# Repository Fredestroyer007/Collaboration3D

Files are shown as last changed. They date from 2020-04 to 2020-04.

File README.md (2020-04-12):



<br />
<br />

Dans ce guide vous allez retrouver toutes les informations requises pour fabriquer vos propres visières par impression 3D pour aider dans la lutte contre COVID-19.

Notre modèle *Jaguar* est une version modifiée du merveilleux modèle conçu par le [Fablab de l'Université Libre de Bruxelles](https://fablab-ulb.gitlab.io/projects/coronavirus/protective-face-shields/). Vous pouvez retrouver leur modèle original [ici](https://gitlab.com/fablab-ulb/projects/coronavirus/protective-face-shields/-/tree/master/PFC-Headband-Light-3DPrint).

Le modèle *Jaguar* peut sembler assez léger et peu résistant, mais je vous assures qu'avec une bonne impression, il est très difficile de casser la visière.

Le coût brut de production estimé est moins de 1$ soit 0,20$ pour le filament, 0,70$ pour la feuille d'acétate et des élastiques. En plus, la durée d'impression par visière est d'environ 20 minutes.

Si vous rencontrer un problème lors de l'impression vous pouvez aller directement à notre [FAQ](#faq). **TODO**

Si vous imprimez le modèle, envoyer nous des photos sur [Facebook](https://www.facebook.com/Collaboration3D/). Nous voulons voir vos résultats!!!

Vous pouvez aussi visiter notre [site web](https://collaboration3d.ca/) pour plus d'information!

Un gros merci à nos commanditaires : le Collège de Bois-de-Boulogne, la fondation de l'Hôpital Sacré-Coeur de Montréal, la firme Laporte et Bureau en gros!

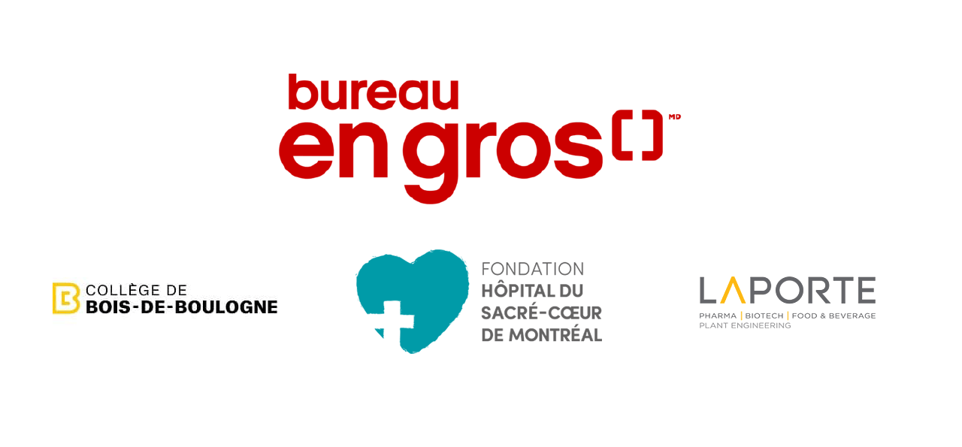
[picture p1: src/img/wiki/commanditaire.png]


Si vous désirez nous commandités, visiter notre [site web](https://collaboration3d.ca/) pour plus d'information!

For the version in English scroll to the end... **TODO**

## Table des matières

* [Pour débuter vous allez avoir besoin de...](#pour-débuter-vous-allez-avoir-besoin-de)
* [Impression 3D](#impression-3d)
  * [Préparation du modèle](#préparation-du-modèle)
    * [Option 1 - Sélectionner un modèle existant](#option-1---sélectionner-un-modèle-existant)
    * [Option 2 - Configurer un modèle selon vos propres besoins](#option-2---configurer-un-modèle-selon-vos-propres-besoins)
      * [Configuration OpenSCAD](#configuration-openscad)
      * [Paramètres](#paramètres)
      * [Exportation](#exportation)
  * [Impression](#impression)
    * [Paramètres obligatoires](#paramètres-obligatoires)
    * [Paramètres optionnels](#paramètres-optionnels)
* [Préparation pour acétate](#préparation-pour-acétate)
* [Préparation pour élastique](#préparation-pour-élastique)
* [Assemblage final](#assemblage-final)
* [Processus de désinfection](#processus-de-désinfection)
* [Avertissement](#avertissement)
* [FAQ](#faq)
* [Auteurs](#auteurs)
* [Licence](#licence)
* [Reconnaissance](#reconnaissance)

## Pour débuter vous allez avoir besoin de...

- Une imprimante 3D 

Tant que la zone d'impression mesure un minimum de 125x125mm vous allez être en mesure d'imprimer les visières. Une surface chauffante est recommendée, mais elle n'est pas essentielle. Utiliser la même méthode d'adhésion que vous utilisez normalement pour du PLA.

- Du filament de type PLA

Peu coûteux, facilement accessible et possible d'imprimer à grande vitesse, le PLA est un matériel idéal pour ce genre d'utilisation. Il faut environ 8g de filament par visière, donc avec une bobine standard de 1kg, vous devriez être en mesure de produire environ 125 visières. Si la production de volume ne vous intéresse pas, vous pouvez aussi utiliser des matériaux comme le PETG, l'ABS, le nylon qui possèdent divers avantages sur le PLA, mais leur vitesse d'impression est plus lente.

- Des feuilles d'acétate de format A4

Vous pourrez en trouver dans les magasins d'articles de bureau.

- Des élastiques

Il faut deux élastiques standard ou vous pouvez concocter votre propre solution pour faire tenir la visière sur la tête.

- Un ordinateur avec [OpenSCAD](https://www.openscad.org/) installé (optionnel) et le logiciel requis pour votre imprimante

Pas besoin d'un ordinateur très puissant, un ordinateur portable fonctionne parfaitement.

- Une perforatrice 3 trous de format nord-américain 4.25" (format de cartable standard au Canada et aux États-Unis)

Plus la capacité est grande, plus votre travail sera facile, vous pourrez faire les trous dans plus d'une feuille d'acétate à la fois.

## Impression 3D
## Préparation du modèle

Sur [la page principale Github](https://github.com/Fredestroyer007/Collaboration3D), cliquer sur « Clone or download » :

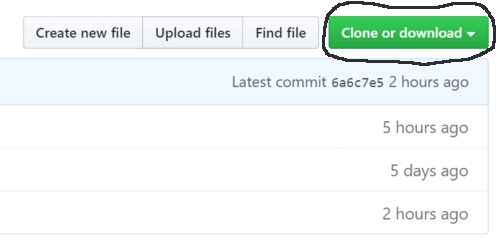
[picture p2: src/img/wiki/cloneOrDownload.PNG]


Ensuite, cliquer sur « Download ZIP » et sélectionner l'endroit que vous désirez télécharger les fichiers sur votre ordinateur :

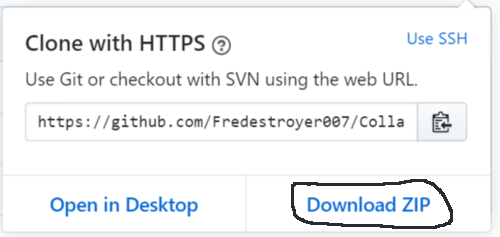
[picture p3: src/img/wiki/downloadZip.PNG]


Ouvrez le dossier compressé et vous avez deux options maintenant.

[La première option](#option-1---sélectionner-un-modèle-existant) est pour un utilisateur moins avancé et [la seconde option](#option-2---configurer-un-modèle-selon-vos-propres-besoins) est pour un utilisateur avancé qui désir optimiser sa production au maximum.

### Option 1 - Sélectionner un modèle existant
Pour débuter, si un modèle existe déjà pour votre configuration d'imprimante, vous devez sélectionner ce modèle. Aller dans le dossier « Modèle », puis « Jaguar ». Ensuite, vous devez sélectionner le dossier correspondant à la hauteur de couche que vous désirez imprimer. À l'intérieur du dossier choisit, vous devez sélectionner le nombre de visière empiler (indiquer par le multiplicateur). Nous vous recommandons de commencer par un nombre plus faible et de lentement augmenter. Vous pouvez ensuite passer à l'étape [Impression](#impression).

### Option 2 - Configurer un modèle selon vos propres besoins!
Si un modèle n'existe pas encore, vous pouvez créer le votre vous-même! La configuration est assez simple!
#### Configuration OpenSCAD
[OpenSCAD](https://www.openscad.org/) est un logiciel gratuit de modélisation CAD paramétrique. Au lieu de modéliser graphiquement un modèle, il est programmer. Cette particularité vous permet d'adapter très facilement le modèle à vos paramètres d'impression.

Après avoir installé [OpenSCAD](https://www.openscad.org/) sur votre ordinateur vous retrouvez le fichier « modification.scad » dans le dossier « CAD » dans le dossier que vous avez télécharger à l'étape précèdente. Cliquer dessus pour lancer le programme :



Une fois dans le programme :

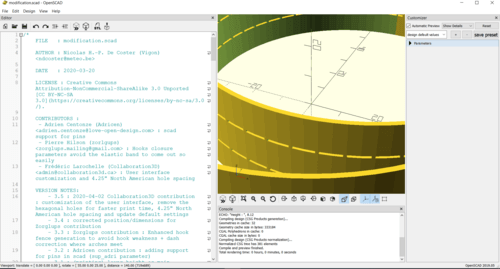
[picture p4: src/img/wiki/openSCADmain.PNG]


Vous pouvez fermer le premier panneau pour créer plus d'espace. Vous n'allez pas avoir besoin de ce panneau. Il s'agit du code source de la pièce :



Sur le panneau de droite « Customizer », cliquer sur « Parameters » pour afficher les paramètres à modifier :

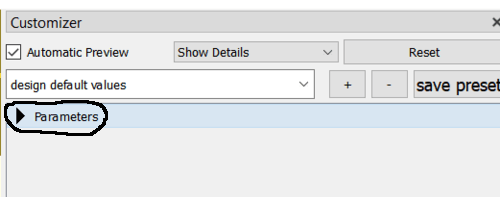
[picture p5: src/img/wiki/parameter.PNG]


Maitenant que l'interface est prêt, à la gauche, vous retrouvez une visualisation de votre modèle et, à la droite, le panneau des paramètres à modifier. Votre interface devrait ressembler à ceci :

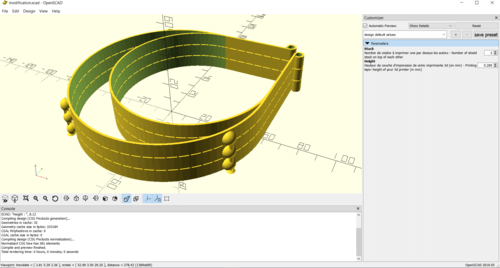
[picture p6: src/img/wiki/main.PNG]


#### Paramètres

Vous avez deux paramètres à modifier. Le premier « Stack » est le nombre de visière empiler que vous désirez imprimer par impression. Nous vous suggérons de commencer par des plus petites valeurs et de lentement augmenter le nombre de visière que vous imprimez à la fois à mesure que vous découvrez les limites de votre imprimante 3D. Le second paramètre est « Height ». Vous devez simplement entrez la valeur de la hauteur d'impression de chaque couche de votre imprimante. Ce paramètre est mieux connu sous le nom anglais « layer height ». Dans les contraintes de votre imprimante, plus ce paramètre est grand, plus l'impression sera rapide. Avec ceci en tête, nous vous recommandons de viser une hauteur de couche de 0.3mm et plus si possible pour votre imprimante. Pour observer l'effet de vos paramètres sur la visualisation, cliquer sur un autre champs de paramètre.

Par exemple, pour une Creality Ender-3, comme paramètre pour débuter, nous vous recommandons d'imprimer trois visières à la fois avec une hauteur de couche de 0.28mm :

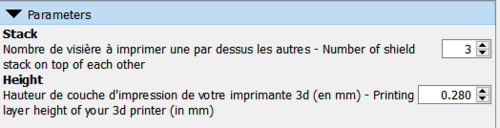
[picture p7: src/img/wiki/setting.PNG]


#### Exportation

Avant d'exporter votre modèle pour impression, vous devez faire le rendu du modèle en cliquant sur F6. Soyez patient. Un modèle volumineux avec plusieurs visières de hauteur peut prendre quelques minutes à faire le rendu. Quand le rendu est finit, vous devriez entendre un son et voir apparaître un message comme celui-ci dans le bas de votre écran :

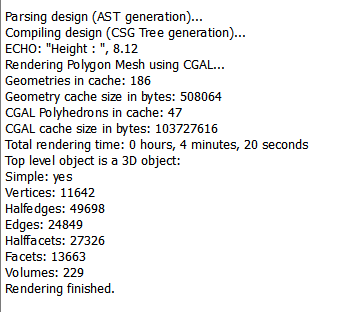
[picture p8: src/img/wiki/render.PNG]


Ensuite, pour exporter le modèle, cliquer sur F7 et sélectionner l'endroit pour sauvgarder le fichier. Garder à l'esprit de lui donner un nom utile, OpenSCAD ne gardera pas vos paramètres en mémoire! Nous vous recommandons de suivre la convention suivante : *Jaguar - (**la hauteur de couche**) - x(**le nombre de visière superposé**).stl*. Donc, par exemple, un fichier avec les paramètres de 0.3mm de hauteur de couche et de 8 visières les unes sur les autres serait nommé : ***Jaguar - .3mm - x8.stl***.

## Impression

Pour débuter, nous vous recommandons de partir de vos paramètres d'impression standard pour votre imprimante pour faire des modifications. Utiliser les paramètres de température recommandé par le fabricant de votre filament.

### Paramètres obligatoires

Pour débuter, dans votre slicer, vous devez sélectionner la même hauteur de couche (« Layer height ») que vous avez sélectionner comme modèle ou dans OpenSCAD. Le but de ce paramètre est de s'assurer que l'espace entre chaque visière soit exactement 2 couches d'impression. Il s'agit probablement d'une hauteur de couches supérieur à ce que vous imprimez normalement, mais le but est d'augmenter la cadence de production. Viser une hauteur de couche de 0.3mm et plus si votre imprimante 3D le permet. 

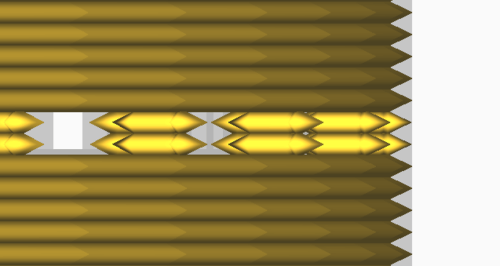
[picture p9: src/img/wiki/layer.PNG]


Le modèle est fait pour être imprimer avec des épaisseurs de branches de 1.2mm. Pour accélérer l'impression et éviter l'utilisation de remplissage (« Infill »), vous devez sélectionner une largeur d'extrusion  (« Extrusion width » ou « Line width ») qui est un multiple de 1.2mm. Les valeurs possibles sont 0.3mm, 0.4mm ou 0.6mm. Garder à l'esprit que la valeur idéale est 0.6mm pour accélérer l'impression. Cependant, une valeur de 0.6mm n'est pas possible avec une buse de 0.3mm, donc pour cette grandeur de buse, limiter la valeur à 0.4mm.

Par le fait même, il faut désactiver toutes formes de remplissage (« Infill ») en sélectionnant une valeur de 0% et sélectionner un nombre de mur assez grand (5-6 murs) pour s'assurer que la visière soit imprimée solide.

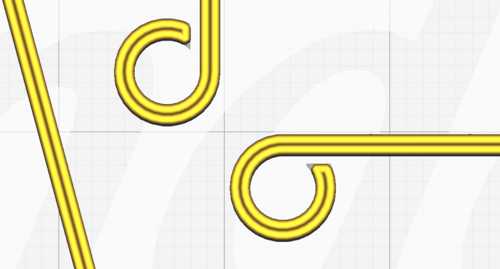
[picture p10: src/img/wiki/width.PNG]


Désactiver toutes formes de support, elles sont déjà intégrer dans le modèle.

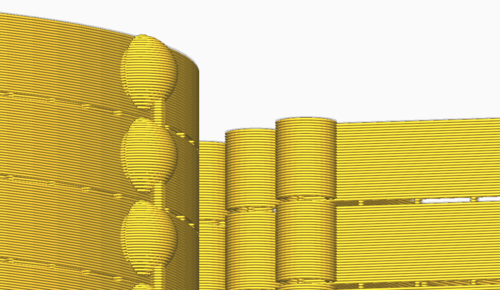
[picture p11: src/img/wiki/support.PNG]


Si la superficie de votre imprimante le permet, vous pouvez imprimer plus d'une tour de visières à la fois. Si vous optez pour cette alternative, garder les crochets les plus près les un des autres pour limiter la durée d'impression.

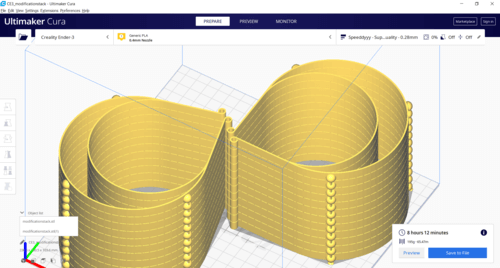
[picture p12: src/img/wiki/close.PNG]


### Paramètres optionnels

Voici quelques paramètres à modifier pour accélérer l'impression pour des utilisateurs avancés. Garder à l'esprit qu'on vise le volume et non la perfection. Aussi, rester à l'intérieur des capacités de votre imprimante. Il est préférable d'imprimer un peu plus lentement que la moitié de vos impressions échoues.

Une vitesse d'impression de plus de 80mm/s devrait être atteignable sur une majorité d'imprimante. Nous vous recommandons de garder la vitesse d'impression de votre premières couches assez lentes (25mm/s) et d'augmenter votre vitesse de déplacement (« Travel ») à plus de 200mm/s.

Si votre imprimante le supporte, vous pouvez augmenter les valeurs d'accélération.

Il ne s'agit que de simples pistes de réflexion. Les paramètres varient énormément d'une imprimante à une autre. Expérimenter! C'est une partie du plaisirs de l'impression 3D!

Comme exemple, voici les paramètres utilisés avec [Cura 4.5](https://ultimaker.com/software/ultimaker-cura) pour une Creality Ender-3 modifié (vous ne serez pas nécessairement en mesure d'atteindre les mêmes vitesses avec une Ender-3, considérer ceci comme une cible) :

« Quality » :
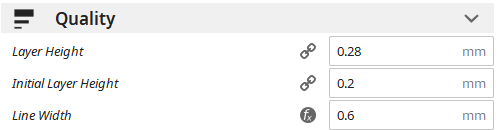
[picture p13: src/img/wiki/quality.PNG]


« Shell » :
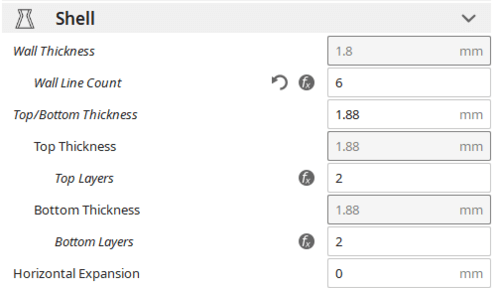
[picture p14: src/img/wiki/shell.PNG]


« Infill » :


« Material » :
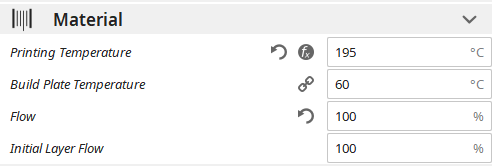
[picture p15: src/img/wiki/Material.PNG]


« Speed » :
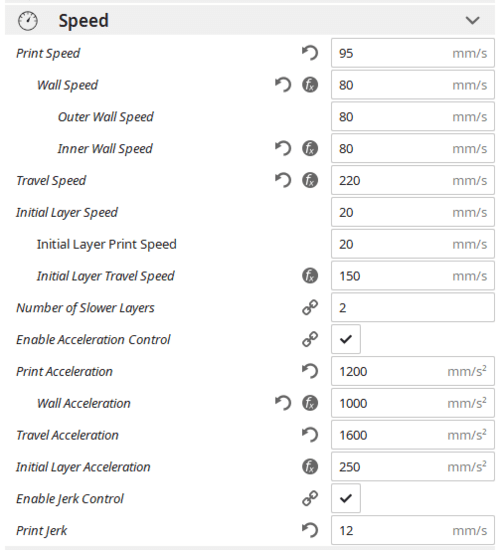
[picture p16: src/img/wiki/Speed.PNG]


« Travel » :
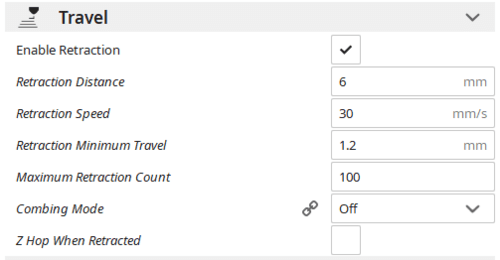
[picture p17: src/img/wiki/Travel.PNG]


« Cooling » :


« Support » :


« Build Plate Adhesion » :


Bonne chance! Persévérez, amusez-vous, c'est le plus important. Il ne faut pas trop se prendre au sérieux :)

# Préparation pour acétate
À l'aide d'une troueuse standard pour faire des trous de cartable (une troueuse qui fait des trous au standard nord-américain 4.25"), faites des trous dans une feuille d'acétate de la même manière que vous faites pour une feuille de papier standard.

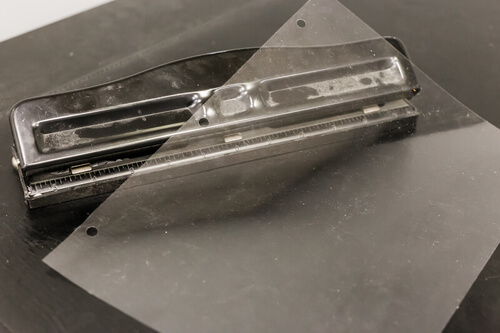
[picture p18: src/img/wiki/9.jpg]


Si la capacité de votre troueuse le permet, nous vous recommandons de faire des trous dans plusieurs feuilles d'acétate à la fois!

# Préparation pour élastique
Attacher deux élastiques ensembles! C'est l'étape la plus simple!

**TODO IMG**

# Assemblage final
L'assemblage final se fait en quelques étapes simples:

1. Laisser votre modèle reposer quelques temps après la fin de l'impression. Vous devez laisser le temps au plastique de bien se refroidir. Vous pouvez profiter de cette période pour inspecter les pièces pour des défauts et des petits bouts de plastiques que vous pouvez retirer.

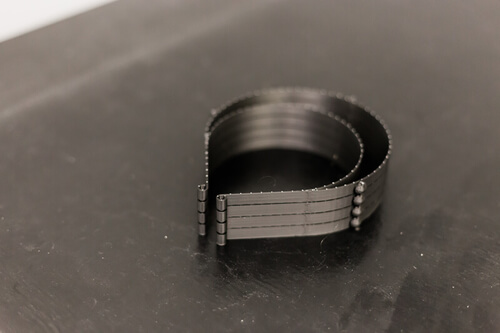
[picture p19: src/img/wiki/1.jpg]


2. En tirant dans des directions opposés, vous devez commencer à séparer les visières des unes des autres. Vous n'avez pas besoin de beaucoup de force. Si les visières sont trop bien attaché ensemble, il y a un problème à quelques parts dans vos paramètres d'impression.

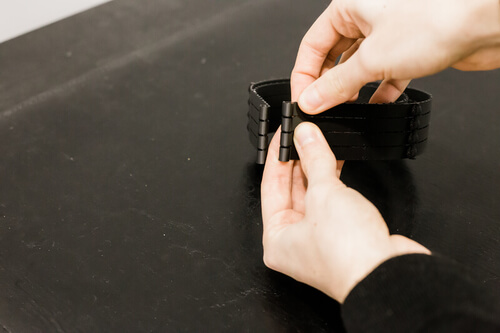
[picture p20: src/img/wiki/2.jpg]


3. Vous pouvez lentement continuer à séparer les visières.

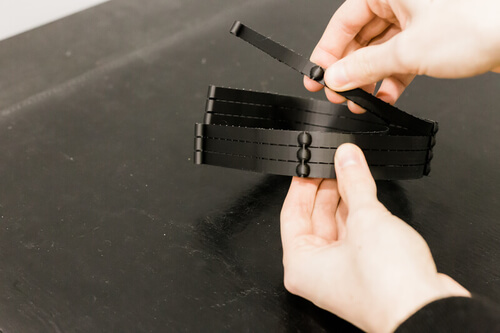
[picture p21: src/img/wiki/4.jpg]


4. La visière est maintenant séparé, veuillez répéter ce processus pour chaque visière.

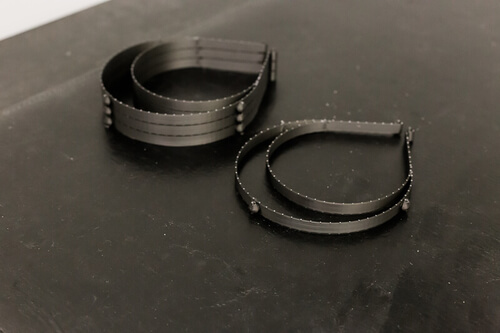
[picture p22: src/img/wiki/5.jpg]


5. Maintenant, avec des pinces à côté coupant, veuillez retirer les support de la visière.

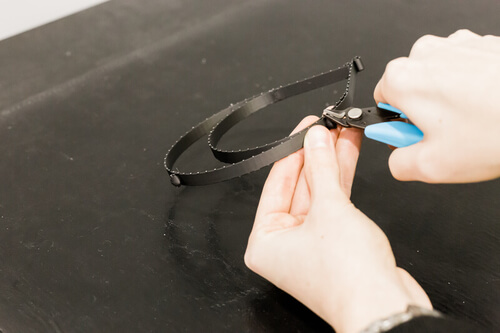
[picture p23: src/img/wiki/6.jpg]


6. Veuillez répéter ce processus pour chaque visière.

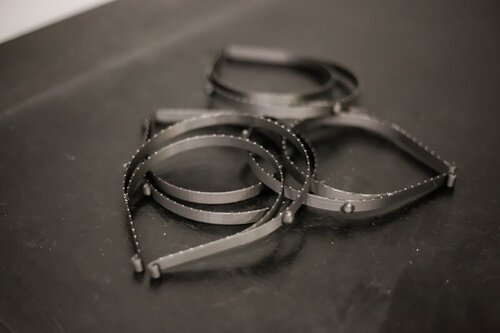
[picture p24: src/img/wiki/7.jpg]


7.Veuillez prendre une visière et une acétate.

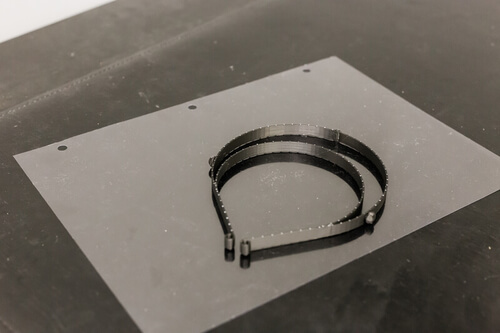
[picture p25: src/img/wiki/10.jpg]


8. Débuter par rentrer la point d'attache du milieu de la visière dans le trous du milieu de la feuille d'acétate.

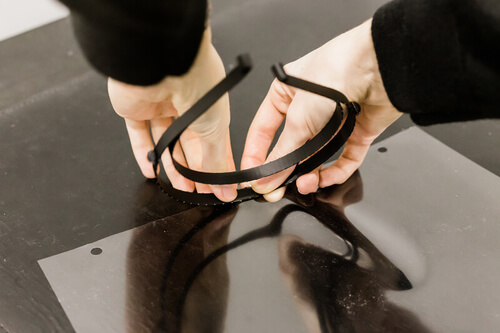
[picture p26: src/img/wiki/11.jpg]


9. Continuer, en effectuant la même manipulation avec les trous de gauches.

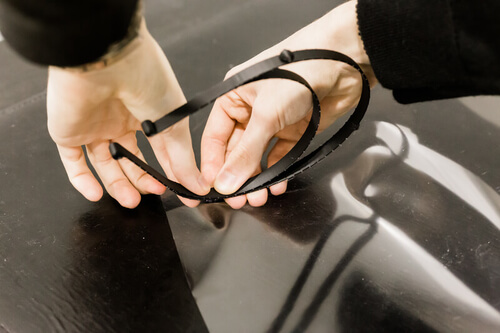
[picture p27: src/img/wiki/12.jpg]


10. Et en effectuant la même manipulation avec les trous de droites.

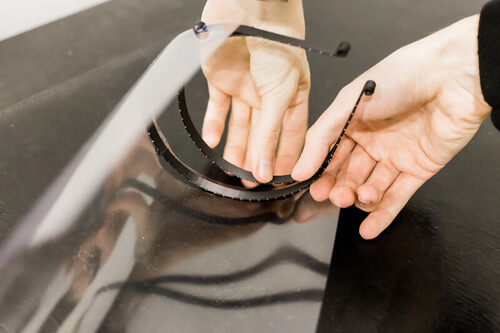
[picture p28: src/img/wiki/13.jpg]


11. Veuillez répéter la même série d'opération (de 7 à 10) avec chacune des visières.
 
**TODO IMG**

12. Attacher les élastiques

**TODO IMG**

13. Vous avez maintenant des visières de protection!

**TODO IMG**

Voilà! L'assemblage est aussi simple!

# Processus de désinfection
Une étape très important est le processus de désinfection de la visière. Une visière contaminé par le coronavirus n'est pas un bon outil pour ce protéger contre COVID-19!

Lors de l'usage de la visière, il est recommandé de la désinfecté périodiquement selon le protocole de la firme Laporte. Cliquer [ici](https://github.com/Fredestroyer007/Collaboration3D/raw/master/src/files/Proc%C3%A9dure_de_d%C3%A9sinfection.pdf) pour télécharger le protocole. Un gros merci à la firme Laporte pour avoir produit ce protocole.

D'autres petites notes à garder en tête lors de la production des visières sont les suivantes :

1. Si vous doutez que vous-même ou un proche puisse être atteint par le COVID-19. Il n'est pas recommandé de produire des visières en raison du risque de propagation.
2. Lors de la production, avant de manipuler des visières, des outils, des imprimantes 3D, veuillez vous lavez les mains durant au moins 20 secondes avec de l'eau tiède et du savon.
3. Lorsque vous manipulez votre imprimante et les visières, veuillez porter une des visières que vous avez fabriquer!
4. Garder tous animaux de compagnie éloigné des visières ou de votre imprimante 3D.
5. Une fois par jour, veuillez désinfecter votre imprimante avec de l'alcool à friction isopropylique.
6. Idéalemment, laisser les visières pour une durée de 3 jours dans un sac en plastique avant de les utiliser. Si ce n'est pas possible, veuillez utiliser le processus de désinfection!

# Avertissement
Ces visières ne sont pas approuvés par Santé Canada. Elles devraient seulement être utilisé en dernier recours, si aucune autres alternatives sont disponibles. Nous dénions formellement toutes responsabilités.

# FAQ

**TODO**

# Auteurs
* **Frédéric Larochelle** - *Travail initial* - [Fredestroyer007](https://github.com/Fredestroyer007)

# Licence 


Ce projet est distribué sous une licence GNU General Public License v3.0 - voir le fichier [LICENSE](LICENSE) pour plus de détails

# Reconnaissance

Un gros merci au [Fablab de l'Université Libre de Bruxelles](https://fablab-ulb.gitlab.io/projects/coronavirus/protective-face-shields/) pour avoir rendu disponible en ligne leur modèle. Vous pouvez retrouver leur modèle original [ici](https://gitlab.com/fablab-ulb/projects/coronavirus/protective-face-shields/-/tree/master/PFC-Headband-Light-3DPrint).

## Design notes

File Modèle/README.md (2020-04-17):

Le dossier « Tigre » contient le modèle Tigre que nous produisons actuellement! Il s'agit du modèle que vous devez imprimer!
Le dossier « Archive » contient le modèle Jaguar qui est plus rapide à imprimer mais moins pratique pour ceux qui les utilisent.

The "Tiger" folder contains the Tiger model we are currently producing! This is the model you should print!
The “Archive” folder, on the other hand, contains the Jaguar models that are faster to print, but less practical for thoses who use them.

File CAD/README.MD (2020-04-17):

**CECI EST SEULEMENT POUR LE MODÈLE "JAGUAR", NOUS IMPRIMONS LE "TIGRE" ACTUELLEMENT**

Le fichier modification.scad est le fichier du modèle paramètrique. Pour un utilisateur normal, vous n'avez pas besoin 
d'utiliser ce fichier. Aller voir le dossier « Modèle » pour des fichiers d'impression .stl déjà fait. Pour un utilisateur 
avancé, veuillez voir le README.md principal pour des instruction sur l'utilisation du fichier modification.scad.

**THIS IS ONLY FOR THE "JAGUAR" MODEL, WE ARE CURENTLY PRINTING THE "TIGRE" MODEL.**

The modification.scad file is the parametric model file. For a normal user, you don't need to use this file. 
Go to the “Modèle” folder for already made .stl print files. For an advanced user, please see the main README.md 
for instructions on using the modification.scad file.

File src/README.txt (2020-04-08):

Vous n'avez pas besoin de regarder ce dossier!!! Il s'agit simplement des fichiers ressources des éléments contenus dans
les instructions!

You don't need to look at this folder!!! These are simply the resource files of the elements contained in
the instructions!

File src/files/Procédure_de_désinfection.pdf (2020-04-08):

PROCEDURE DE Désinfection des Visières de protection pour les travailleurs de la santé

### 1. OBJECTIF

Définir une méthode standardisée pour désinfecter les visières qui serrent à la protection

des travailleurs pour la santé ainsi que leur environnement,

### 2. PORTÉE

Cette procédure s’applique aux visières, à ses différentes composantes et à leur emballage

primaire. De plus, l’environement en contact avec

### 3. MATÉRIEL REQUIS

- Alcool isopropylique à 70%
- Essuie-tout ou linge propre
- Gants de protection en latex

### 4. PROCÉDURE

1. Mettez des gants en latex
2. Vaporiser les deux mains portantes des gants avec de l’alcool isopropylique à

70%

3. Laisser sécher pendant 1 minute
4. Nettoyage de l’environnement de travail:
a. Vaporisez toutes les surfaces qui sont utilisées pour fabriquer et

assembler la visière avec de l’alcool isopropylique à 70%

b. En utilisant un linge propre ou un essuie-tout, nettoyer de la gauche

vers la droite, en commençant par la section la plus propre, jusqu’à ce

que toute la surface soit couverte (voir figure 1 ci-dessous)

5. Nettoyage de l’emballage primaire de la visière
a. Pulvérisez la section interne de l’emballage avec de l’alcool

isopropylique à 70%

PROCEDURE DE Désinfection des Visières de protection pour les travailleurs de la santé

6. Nettoyage de la visière assemblée:
a. Vaporiser la première face de la section transparente de la visière avec

de l’alcool isopropylique à 70%

b. En utilisant un linge propre ou un essuie-tout, nettoyer de la gauche

vers la droite, en commençant par la section la plus propre, jusqu’à ce

que toute la surface soit couverte (voir figure 1 ci-dessous)

c. Répéter les étapes 6a et 6b ci-dessus pour la deuxième face de la section

transparente de la visière

d. Imbiber le linge propre ou essuie-tout avec de l’alcool isopropylique à

70%

e. Nettoyer toutes les surfaces du support de la visière ainsi que l’élastique

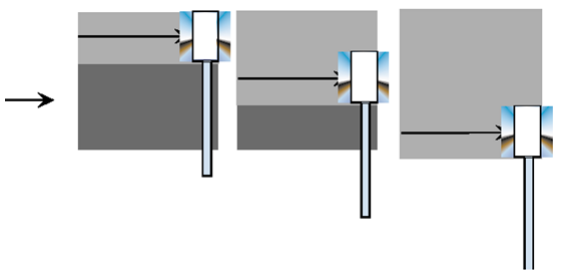
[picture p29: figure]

Figure 1 _ Technique de nettoyage

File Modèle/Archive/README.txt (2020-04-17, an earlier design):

Tigre est le modèle original que nous avons distribuer à l'hôpital Sacré-Coeur de Montréal.Il s'agit d'une version modifier du modèle de Prusa https://www.prusaprinters.org/prints/25857-prusa-face-shield.

Tigre is the original model that we have distributed at the Sacré-Coeur hospital in Montreal. It is a modify version of the model from Prusa Research https://www.prusaprinters.org/prints/25857-prusa-face-shield.

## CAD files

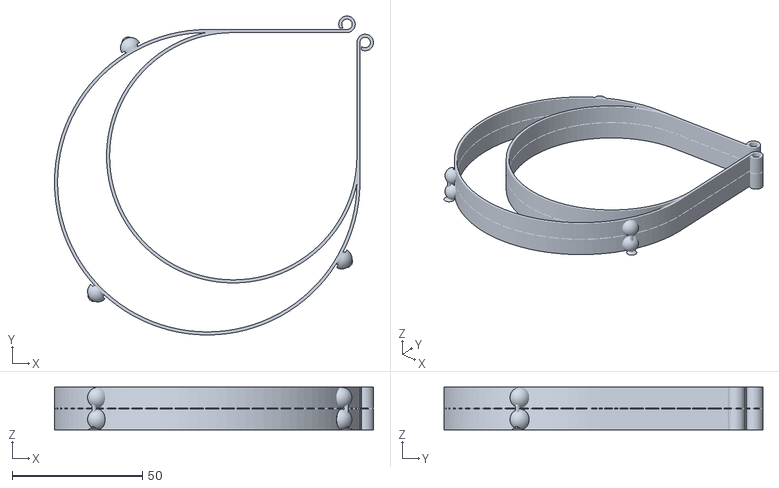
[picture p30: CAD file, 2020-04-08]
Modèle/Jaguar/Jaguar - .20mm/Jaguar - .20mm - x2.stl
122.6 x 122.6 x 16.4

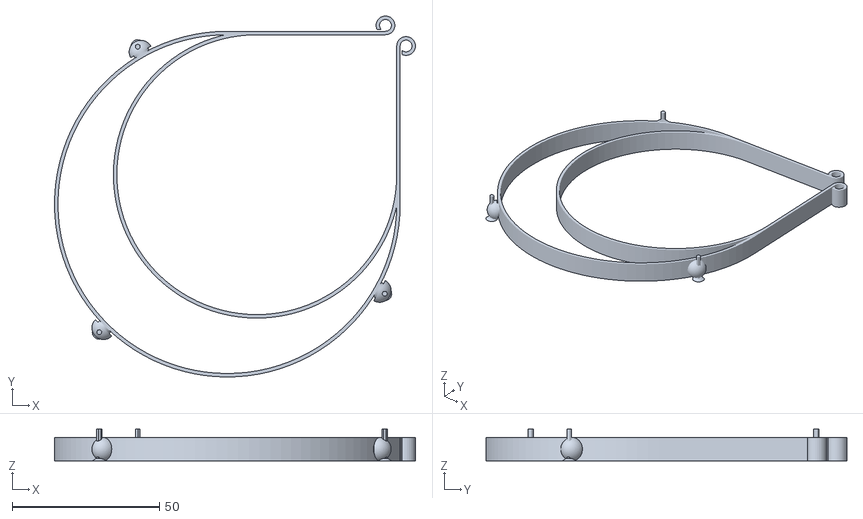
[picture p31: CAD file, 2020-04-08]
Modèle/Jaguar/Jaguar - .25mm/Jaguar - .25mm - x1.stl
122.6 x 122.6 x 10.8

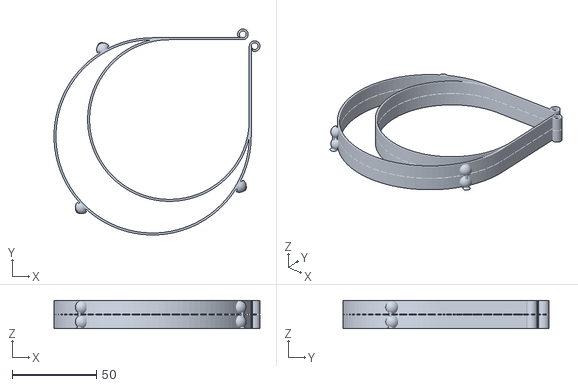
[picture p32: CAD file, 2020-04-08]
Modèle/Jaguar/Jaguar - .28mm/Jaguar - .28mm - x2.stl
122.6 x 122.6 x 16.8

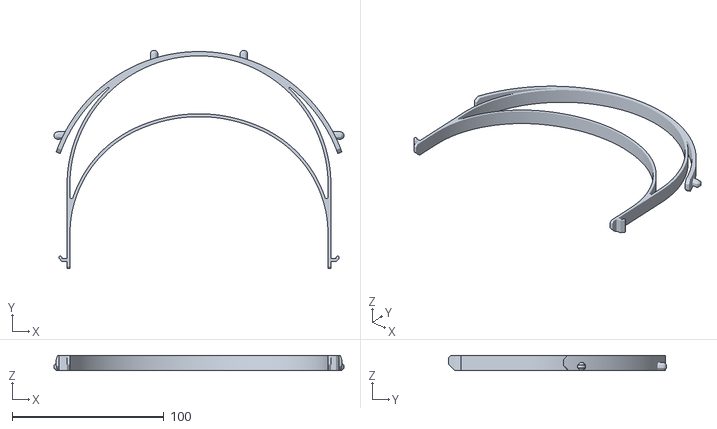
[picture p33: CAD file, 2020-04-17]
Modèle/Tigre/Tigre.stl
191.0 x 143.7 x 9.70

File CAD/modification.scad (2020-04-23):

/*
    FILE   : modification.scad
    
    AUTHOR : Nicolas H.-P. De Coster (Vigon) <ndcoster@meteo.be>
    
    DATE   : 2020-03-20
    
    LICENSE : Creative Commons Attribution-NonCommercial-ShareAlike 3.0 Unported [CC BY-NC-SA 3.0](https://creativecommons.org/licenses/by-nc-sa/3.0/).
    
    CONTRIBUTORS : 
     - Adrien Centonze (Adricen) <adrien.centonze@love-open-design.com> : scad support for pins
     - Pierre Hilson (zorlgups) <zorglups.mailing@gmail.com> : Hooks closure parameters avoid the elastic band to come out so easily
     - Frédéric Larochelle (Collaboration3D) <admin@collaboration3d.ca> : User interface customization, hook modification and 4.25" North American hole spacing
     
    VERSION NOTES:
        - 3.6 : 2020-04-22 Collaboration3D contribution : hook modification for less accurate printer
        - 3.5 : 2020-04-02 Collaboration3D contribution : customization of the user interface, remove the hexagonal holes for faster print time, 4.25" North American hole spacing and update default settings
        - 3.4 : corrected position/dimensions for Zorglups contribution
        - 3.3 : Zorglups contribution : Enhanced hook fence generation to avoid hook weakness + dash correction where arches meet
        - 3.2 : Adricen contribution : adding support for pins in scad (sup_adri parameter)
        - 3.1 : (printing) layer height as main parameter for stacked distance and piece height automatic rounding (better slicing/printing results with thick layers)
        - 3.0 : 2020-03-25 : automatic calculation no matter the number of pins, placing them properly on circle or temple depending on fix_dist parameter
        - 2.3 : corrected bug : proper hook support
        - 2.1 : corrected bug : no more parity issue with dash line
        - 2.0 : stackable version, automatically calculated dashet support
        - 1.1 : lowered pins (limiting support)
        - 1.0 : added central pin (was avoided previously because more complex punch in transaprent foil but asked explicitely by St Pierre Hospital, thus added)
        - 0.2 : adapted pins size and position
        - 0.1 : second draft : added pins for foil clipping
        - 0.0 : first draft : clipping system
//*/

//Customizer

//Nombre de visière à imprimer une par dessus les autres - Number of shield stack on top of each other
Stack = 3;

//Hauteur de couche d'impression de votre imprimante 3d (en mm) - Printing layer height of your 3d printer (in mm)
Height = 0.28;


/* [Hidden] */
//General params
n_stacked = Stack;    //vertical repeat
layer_h   = Height;  //printing layer height : will be used to adjust sizes so that they remain exact integer multiples of the layer height value. Piece height ([height]) and distance between stacked pieces ([stacked_d]) are the rounding targeted values.
stacked_d = 2*layer_h;  //distance between stacked pieces (better use integer multiple of your layer height)
e=0.01;           //general purpose "epsilon value" for better preview rendering (avoid artifacts)


//Dashes (support for stacking)
dash_l    = .8;    //dash length
dash_int  = 6;     //dash interval
sup_adri  = true; //set to "true", will add vertical supports under pins, (adricen contribution)

//Main parameters
out_d     = 115;  //inside diameter of outer ring
in_d      = 95;   //inside diameter of inner ring
approx_h  = 8;    //height of the module (approximative, will be adjusted to be an integer multiple value of layer_h)
sec       = 5;    //setback from joining branches
th        = 1.2;  //thickness of module (=0.4*3 or 0.6*2 for printing speed optimization)
hook_d    = 4;    //hooks diameter
hook_fence = 1.2; //fence width (the smaller, the better it holds the elastic bands)


//Fixing pins
fix_n    = 3;     //number of pins
fix_dist = 215.9; // distance between the extreme mounting pins
fix_d = 5.5; //diameter of the mounting pins
fix_h = 4; //pin lenght
fix_over = 1.2;


height = round(approx_h/layer_h)*layer_h;
echo("Height : ", height);
out_r = out_d/2;
in_r  = in_d/2;
hook_r = hook_d/2;
holes_d = height/2;
fix_r = fix_d/2;

for(i=[0:n_stacked-1]){
    
translate([0,0,i*(height+stacked_d)])
union(){

  structure(out_d, in_d, hook_d, height, th);

  arc_l = PI*(out_d+2*th)*3/4;
  fix_int = fix_dist/(fix_n-1);
  mid_pos = (fix_n-1)/2;
  alpha_int = 360*fix_int/(PI*(out_d+2*th));
  /*
  // Fixings
  */
  
  for(p = [0:fix_n-1]){
      pos_n = p-mid_pos;
      alpha = pos_n * alpha_int;
      if(alpha < -135){
        translate([(fix_dist-arc_l)/2,0,0])
          rotate([0,0,-135]){
            translate([0,0,height/2])
              rotate([-90,0,135])
              translate([0, 0, out_r ])
              fixing(d=fix_d, h=fix_h+th, over=fix_over);
          if(sup_adri){
            rotate([-90,0,135])
              translate([0, 0, out_r+4 ])
              rotate([90,0,0])
              supports(i);
        }
          }
      }
      else if(alpha > 135){
        translate([0,(fix_dist-arc_l)/2,0])
          rotate([0,0,135]){
            translate([0,0,height/2])
              rotate([-90,0,135])
              translate([0, 0, out_r ])
              fixing(d=fix_d, h=fix_h+th, over=fix_over);
            if(sup_adri){
              rotate([-90,0,135])
                translate([0, 0, out_r+4 ])
                rotate([90,0,0])
                supports(i);
            }
          }
      }
      else{
        rotate([0,0,alpha]){
          translate([0,0,height/2])
            rotate([-90,0,135])
            translate([0, 0, out_r ])
            fixing(d=fix_d, h=fix_h+th, over=fix_over);
          if(sup_adri){
            rotate([-90,0,135])
              translate([0, 0, out_r+4 ])
              rotate([90,0,0])
              supports(i);
          }
        }
      }
  }
/*
  %translate([out_r+th, (fix_dist-arc_l)/2,height/2])
    rotate([0,90,0])
      fixing(d=fix_d, h=fix_h, over=fix_over);
  %translate([(fix_dist-arc_l)/2,out_r+th,height/2])
    rotate([-90,0,0])
      fixing(d=fix_d, h=fix_h, over=fix_over);  
  */

    

}
//support
if(i != n_stacked-1){
  translate([0,0,i*(height+stacked_d)+height])
    structure(out_d, in_d, hook_d, stacked_d, th, isStruct=true);
}
}

/*////////////////
// M O D U L E S 
*/////////////////
module empty_cyl(in_d, th, h, dashed=false){
  difference(){
    cylinder(d=in_d+2*th, h=h);
    translate([0,0,-e])cylinder(d=in_d, h=h+2*e);
    if(dashed){
        circ = PI*(in_d+th/2);
        n_cube_dash = ceil(circ/dash_int);
        alpha = 360/n_cube_dash;
        for(i=[0:n_cube_dash-1]){
            rotate([0,0,i*alpha+30]) //+30 cheating to get proper hooks support (dirty but works)
            translate([in_d/2+th,0,h/2])
              cube([in_d/2+th+e, dash_int-dash_l, h+2*e], center=true);
        }
    }
  }
}

module temple(l,w,h,dashed=false){
  difference(){
    cube([l,w,h]);
    if(dashed){
      n_dash = ceil(l/dash_int);
      for(i=[0:n_dash]){
        translate([dash_l+dash_int*i,-e,-e])cube([dash_int-dash_l, w+2*e, h+2*e]);
      }
    }
  }
}

module arc3_4(in_d, th, h, dashed=false){
  difference(){
    empty_cyl(in_d, th, h, dashed=dashed);
    translate([0,0,-e])cube([in_d, in_d, h+2*e]);
  }
}

module clip(h,w,th,clip_solid){
  difference(){
    cube([w,h,clip_solid]);
    translate([th,th,-e/2])cube([th,h-2*th, clip_solid+e]);
    translate([w-2*th,th,-e/2])cube([th,h-2*th, clip_solid+e]);
    translate([th,h-2*th,-e/2])cube([w-2*th,th, clip_solid+e]);
    translate([3*th,2*th,-e/2])cube([th, h-5*th, clip_solid+e]);
    translate([3*th,th,-e/2])cube([w-6*th, th, clip_solid+e]);
    translate([3*th,2*th+(h-8*th)/3,-e/2])cube([w-6*th, th, clip_solid+e]);
    translate([3*th,2*th+2*((h-8*th)/3)+th,-e/2])cube([w-6*th, th, clip_solid+e]);
    translate([3*th,h-4*th,-e/2])cube([w-6*th, th, clip_solid+e]);
  }
    
}

module fixing(d, h, over){
    sph_d = d+2*over;
    cylinder(d=d, h=h-d/2, $fn=50);
    translate([0,0,h-d/2])difference(){
      sphere(d=sph_d, $fn=50);
    translate([0,0,-sph_d/2])cube([sph_d,sph_d,sph_d], center=true);
    }
}

module structure(out_d, in_d, hook_d, height, th, isStruct=false){
    out_r = out_d/2;
    in_r = in_d/2;
    hook_r = hook_d/2;
    arc_dist = 3*PI*in_d/4;
    n_holes = floor(arc_dist/height);
/*
// Arcs
*/
arc3_4(out_d, th, height, dashed=isStruct,$fn=100);
difference(){
  translate([out_r-in_r, out_r-in_r, 0])arc3_4(in_d, th, height, dashed=isStruct, $fn=100);
}

/*
// Temples
*/
translate([0, out_r, 0])
  temple(out_r+th-sec, th, height, dashed=isStruct);
translate([out_r+th, 0, 0])
  rotate([0,0,90])
  temple(out_r+th-sec, th, height, dashed=isStruct);
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

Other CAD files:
Modèle/Jaguar/Jaguar - .30mm/Jaguar - .3mm - x1.stl
Modèle/Jaguar/Jaguar - .35mm/Jaguar - .35mm - x2.stl
Modèle/Jaguar/Jaguar - .20mm/Jaguar - .20mm - x1.stl
Modèle/Jaguar/Jaguar - .25mm/Jaguar - .25mm - x2.stl
Modèle/Jaguar/Jaguar - .28mm/Jaguar - .28mm - x1.stl
Modèle/Jaguar/Jaguar - .30mm/Jaguar - .3mm - x2.stl
Modèle/Jaguar/Jaguar - .35mm/Jaguar - .35mm - x1.stl
Modèle/Archive/Jaguar/Jaguar - .30mm/Jaguar - .3mm - x2.stl
Modèle/Archive/Jaguar/Jaguar - .35mm/Jaguar - .35mm - x1.stl
Modèle/Archive/Jaguar/Jaguar - .20mm/Jaguar - .20mm - x1.stl
Modèle/Archive/Jaguar/Jaguar - .25mm/Jaguar - .25mm - x2.stl
Modèle/Archive/Jaguar/Jaguar - .28mm/Jaguar - .28mm - x1.stl
Modèle/Archive/Jaguar/Jaguar - .30mm/Jaguar - .3mm - x1.stl
Modèle/Archive/Jaguar/Jaguar - .35mm/Jaguar - .35mm - x2.stl

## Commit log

2020-04-03 Upload CAD
    [modification.scad]
2020-04-08 Rename .stl
    [0.25mmx1.stl, 0.25mmx2.stl, Jaguar - .20mm - x1.stl, Jaguar - .20mm - x2.stl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]
2020-04-09 Add assembly image
2020-04-17 Create Jaguar - .20mm
2020-04-17 Create Jaguar - .25mm
2020-04-17 Create Jaguar - .28mm
2020-04-17 Create Jaguar - .30mm
2020-04-17 Create Jaguar - .35mm
2020-04-23 3.6 openscad
    [modification.scad]
